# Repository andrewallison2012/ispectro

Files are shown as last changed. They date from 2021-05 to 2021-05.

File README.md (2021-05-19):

# Ispectro
Open-source software for an Impedance Spectroscopy (BIS) Device based on Arduino.

To in a venv install:
```
pip install -r requirements.txt 
```

To run:
```
python main.py
```

Qt5 Designer file:
```
ispectro_xml.ui
```

Persistent Settings:
```
config.ini
```

Generate pyQt5 Ui_MainWindow and QtBaseClass classes for python
```
pyuic5 -x ispectro_xml.ui -o ispectro_xml.py
```

Arduino Code for BIS Device
```
firmware.ino
```

KiCad Schematics for Device:
```
impedance_777/impedance_777_r1.pro
```

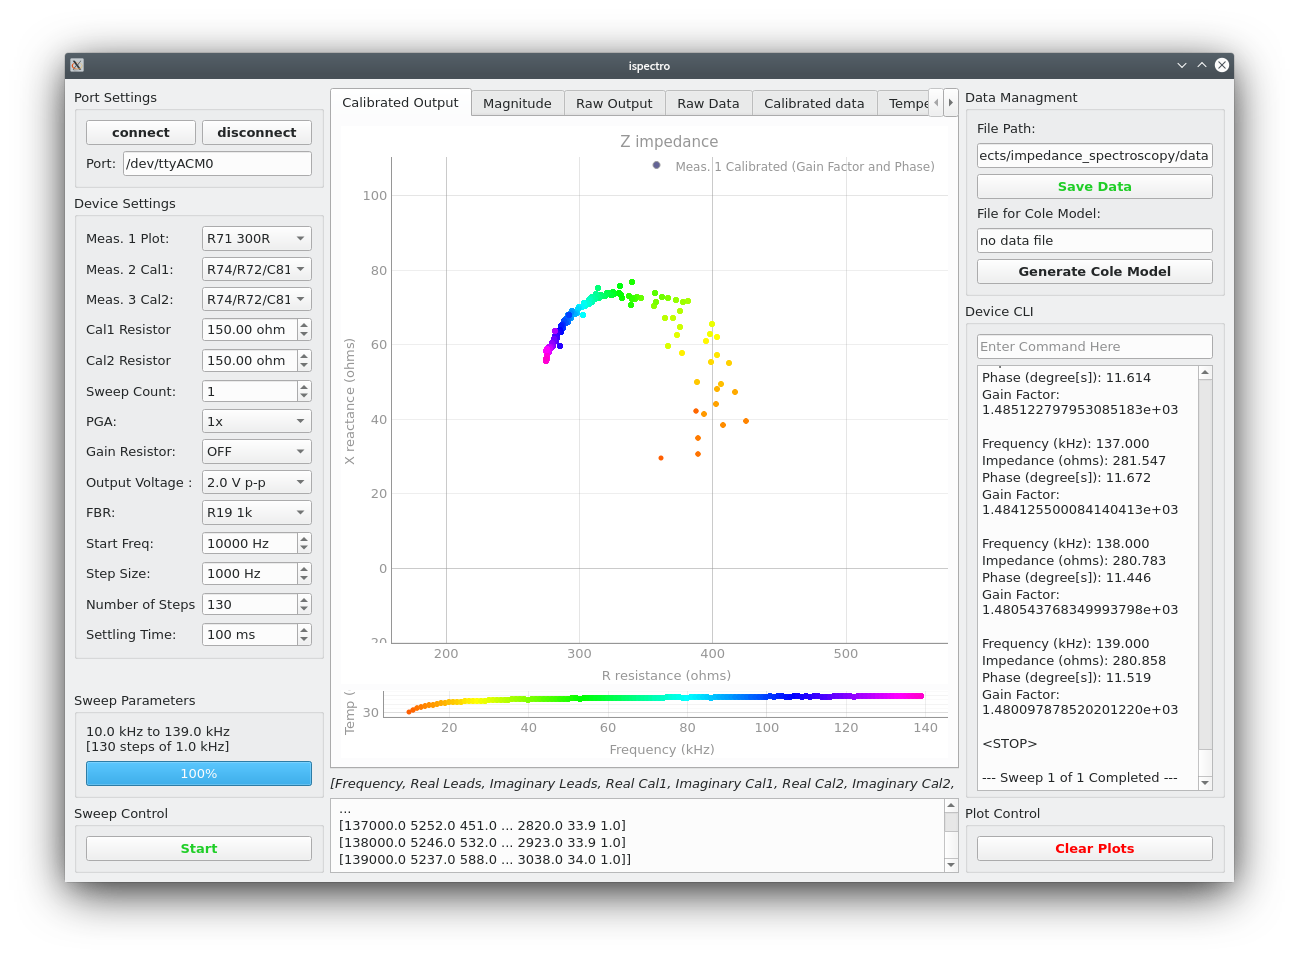
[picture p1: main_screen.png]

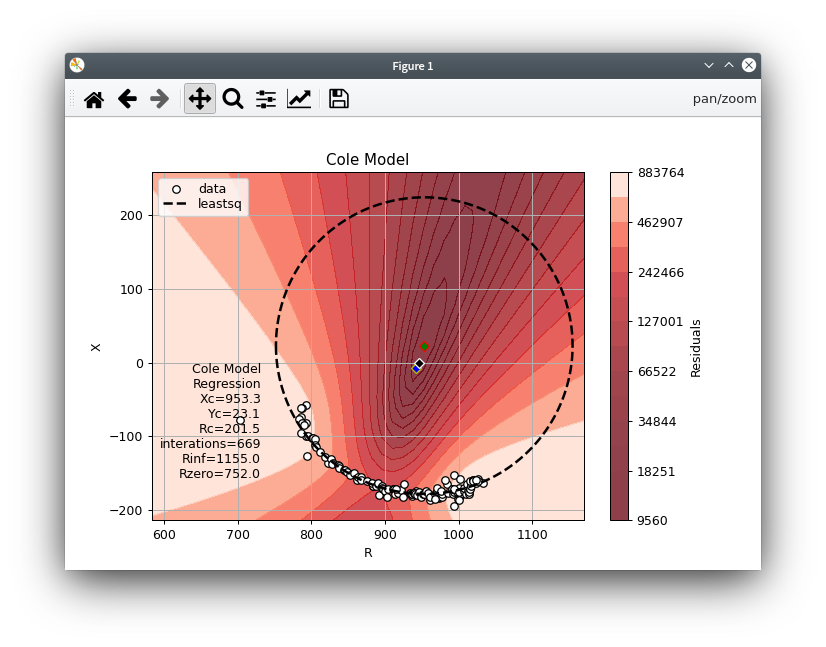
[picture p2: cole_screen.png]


> Software and firmware for an Impedance Spectroscopy (BIS) Device based on ATMEGA2560 (Arduino) and AD5933
>
> Copyright (C) 2021  Andrew Allison
>
> This program is free software: you can redistribute it and/or modify it under the terms of the GNU Affero General Public License as published by the Free Software Foundation, either version 3 of the License, or (at your option) any later version.
>
> This program is distributed in the hope that it will be useful, but WITHOUT ANY WARRANTY; without even the implied warranty of MERCHANTABILITY or FITNESS FOR A PARTICULAR PURPOSE.  See the GNU Affero General Public License for more details.
>
> You should have received a copy of the GNU Affero General Public License along with this program.  If not, see <http://www.gnu.org/licenses/>.



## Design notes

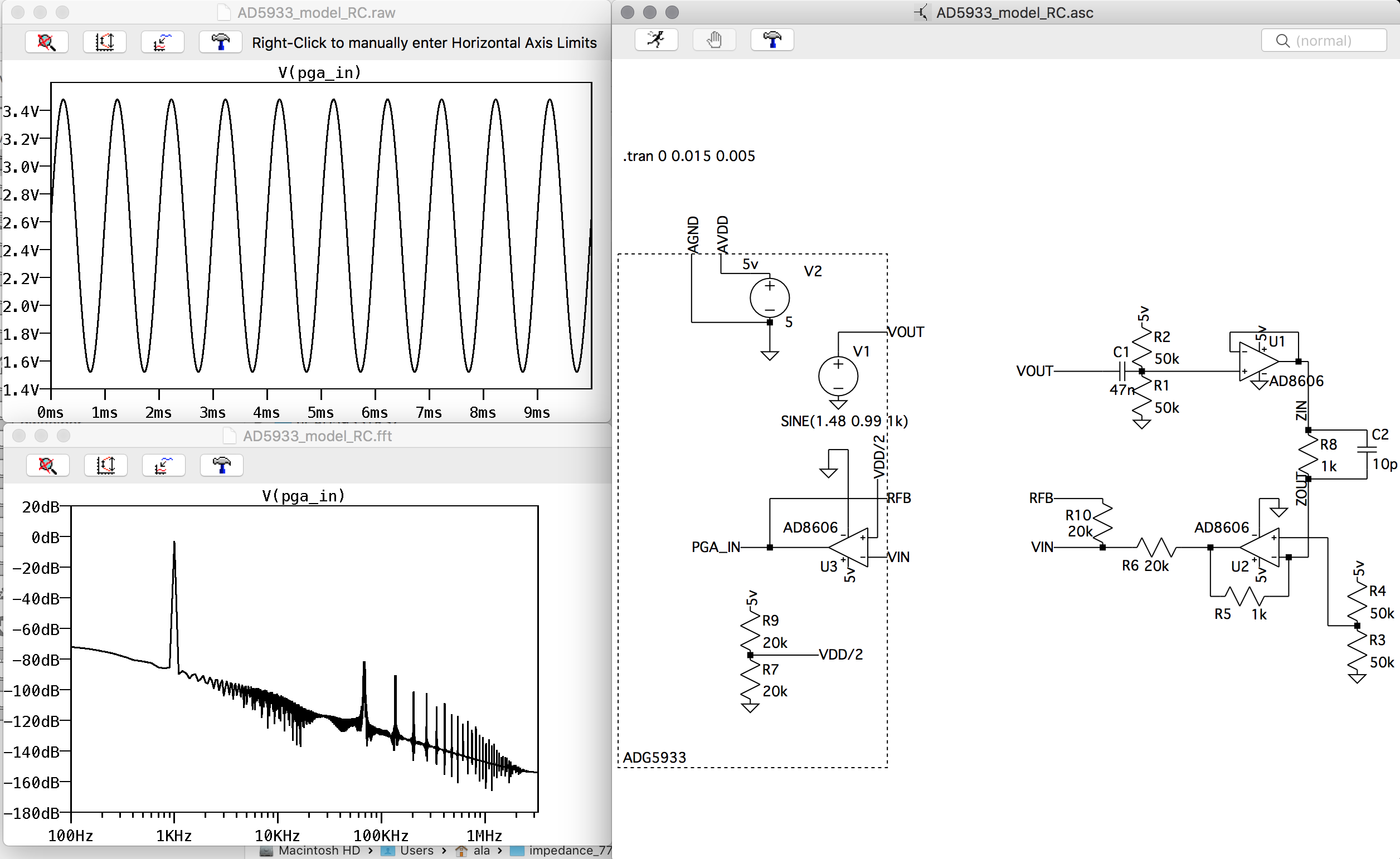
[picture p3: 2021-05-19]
impedance_777/impedance-demo/Screen Shot 2019-07-26 at 9.22.20 PM.png

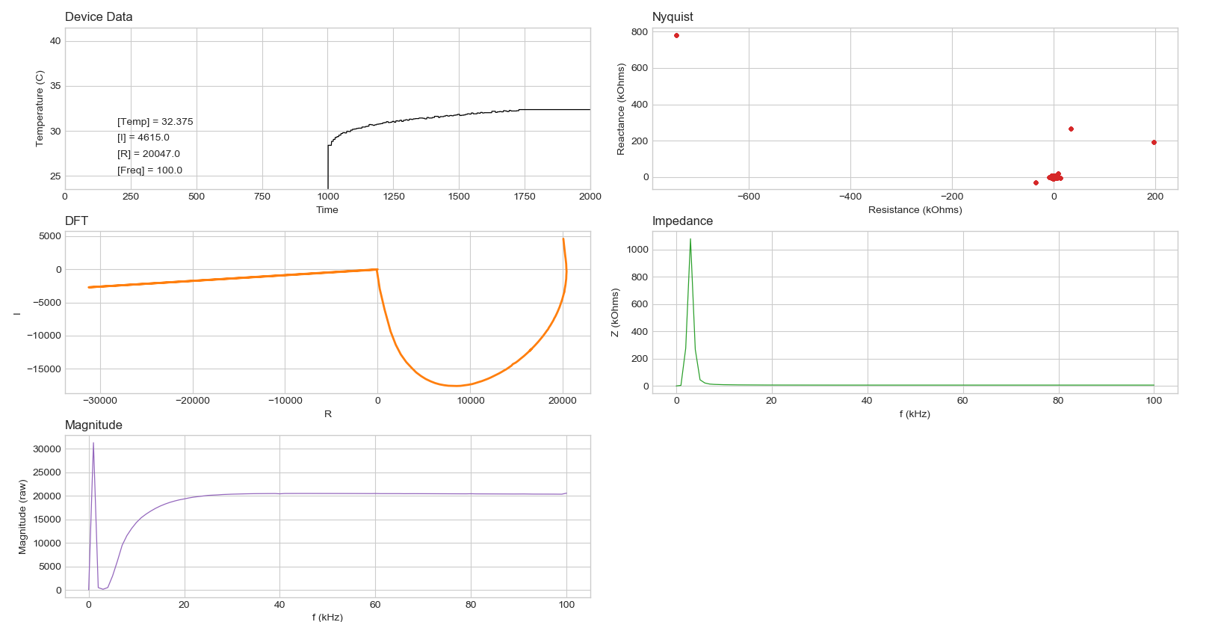
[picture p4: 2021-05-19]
impedance_777/screen-shots/cal6-image.png

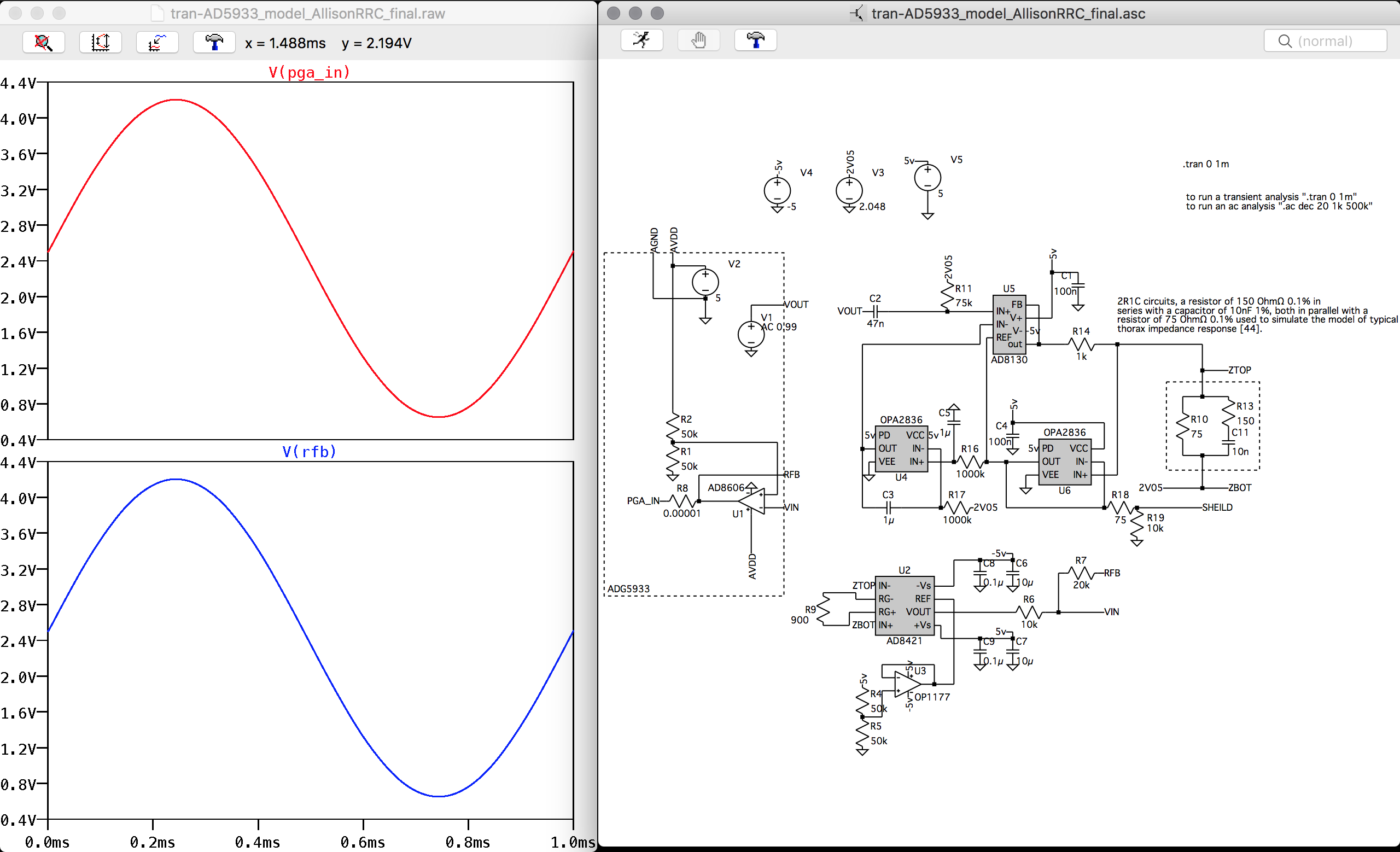
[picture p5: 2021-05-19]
impedance_777/impedance-demo/Screen Shot 2019-10-14 at 8.44.11 PM.png

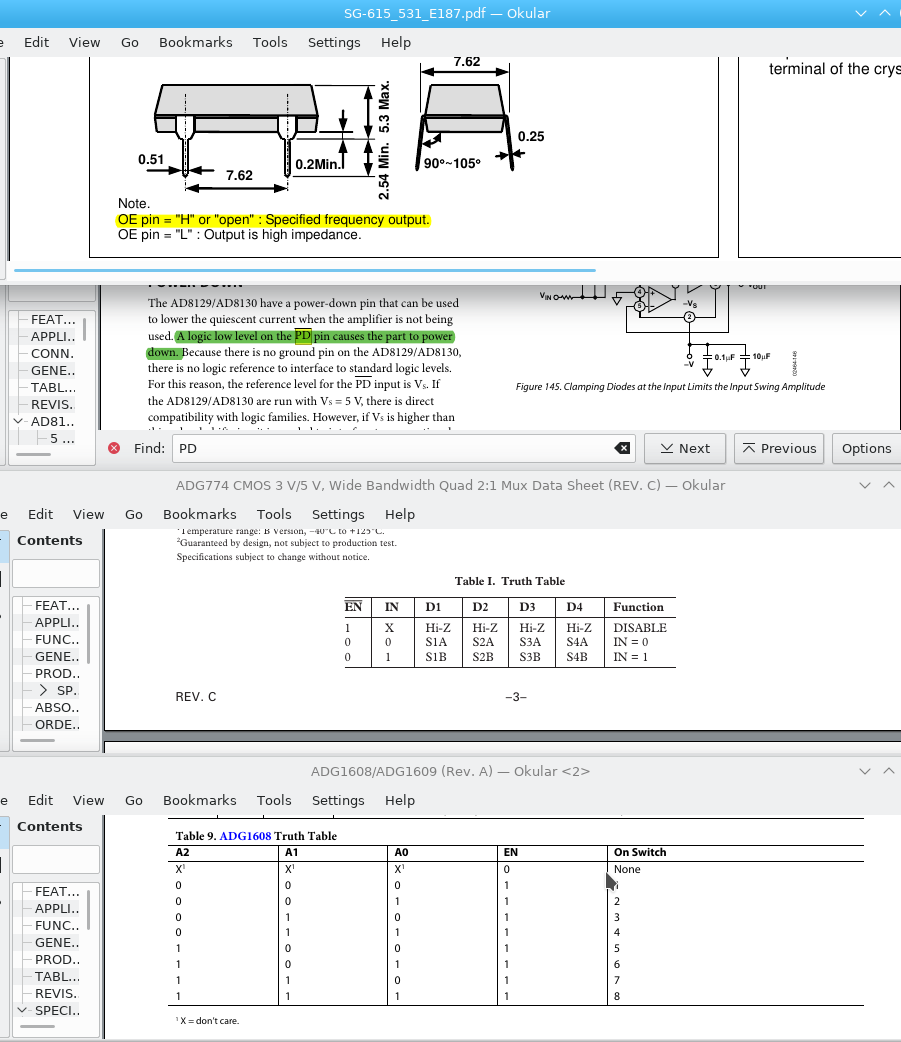
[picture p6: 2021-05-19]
impedance_777/pin_settings_for_impedance_device.png

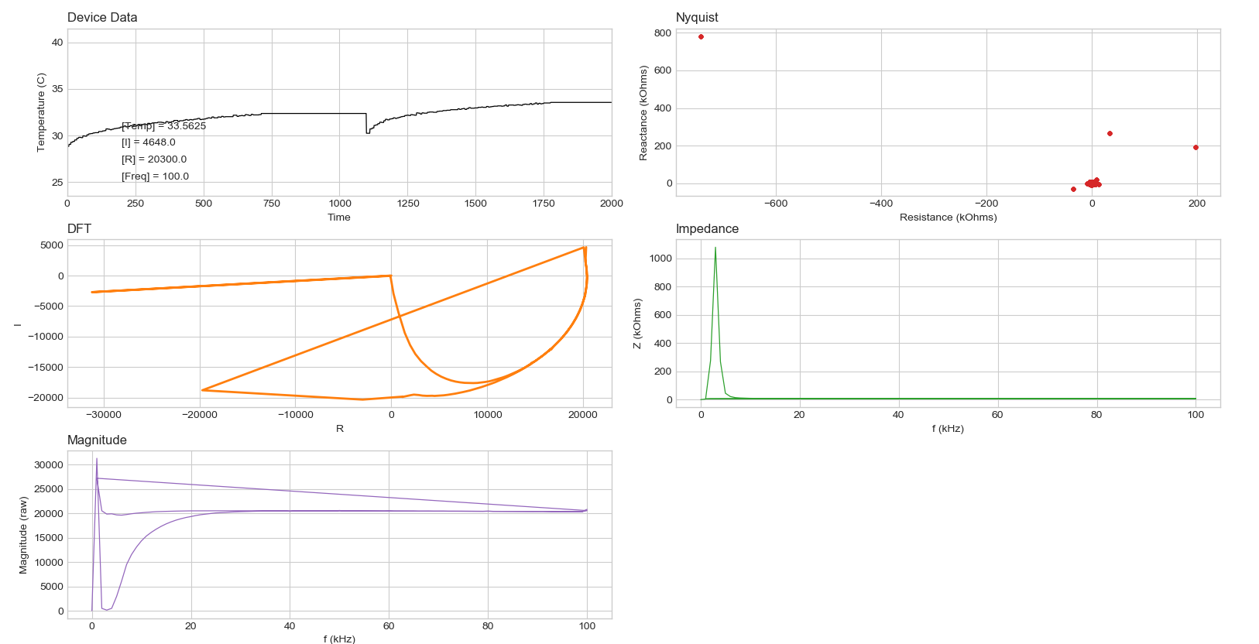
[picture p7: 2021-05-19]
impedance_777/screen-shots/cal6-cal7image.png

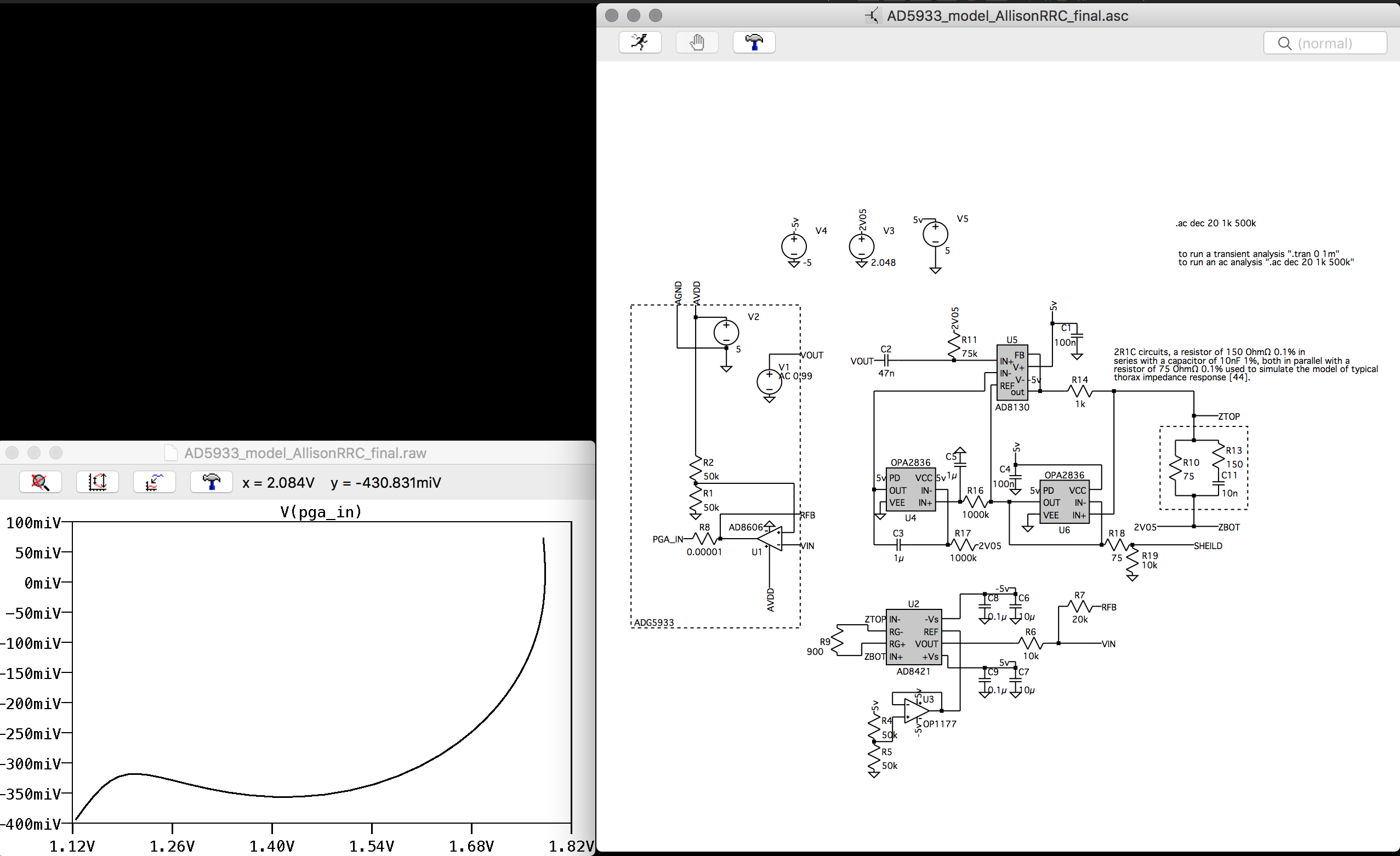
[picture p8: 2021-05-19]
impedance_777/impedance-demo/Screen Shot 2019-08-03 at 2.26.41 PM.png

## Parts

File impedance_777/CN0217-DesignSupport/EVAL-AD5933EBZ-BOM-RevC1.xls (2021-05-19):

Analog Bill Of Materials for EVAL-AD5933EBZ (Rev C1) 13/3/12
Name | Part Description | Value | Tolerance | PCB Decal | SMD | Layer Name | PART DESC | MFG #1 | Part Number | STOCK CODE
C1 | CAP | DNI |  | CAP\MR04 | No | Top | Place holder | n/a | n/a | Not Inserted
C2 | CAP | DNI |  | CAP\MR04 | No | Top | Place holder | n/a | n/a | Not Inserted
C3 | CAP | DNI |  | CAP\MR04 | No | Top | Place holder | n/a | n/a | Not Inserted
Z | CAP | DNI |  | CAP\MR04 | No | Top | Place holder - Insert 2 Wire-Wrap Pins | Analog Issue | 73017015 | ADI Stores 73017015 (x2)
C5 | CAP+ | 10uF |  | CAP\TAJ_B | Yes | Top | 10V Tantalum Capacitor | AVX | TAJB106K016R | FEC 498-737
C6 | CAP | 0.1uF | 10% | 0603 | Yes | Top | 50V X7R SMD Ceramic Capacitor | AVX | 06035C104KAT2A | FEC 1301804
C7 | CAP | 47nF | 10% | R1/8W | No | Top | CAPACITOR, 47NF, 50V, ThruHole | Multicomp | MCRR50473X7RK0050 | FEC 1216439
C8 | CAP | 0.1uF | 10% | 0603 | Yes | Top | 50V X7R SMD Ceramic Capacitor | AVX | 06035C104KAT2A | FEC 1301804
C9 | CAP | 10uF |  | 0805 | Yes | Top | X5R Ceramic Capacitor | Yageo | CC0805KKX5R6BB106 | FEC 9402136
C10 | CAP | 0.1uF | 10% | 0603 | Yes | Top | 50V X7R SMD Ceramic Capacitor | AVX | 06035C104KAT2A | FEC 1301804
C11 | CAP | 10uF |  | 0805 | Yes | Top | X5R Ceramic Capacitor | Yageo | CC0805KKX5R6BB106 | FEC 9402136
C12 | CAP | 0.1uF | 10% | 0603 | Yes | Top | 50V X7R SMD Ceramic Capacitor | AVX | 06035C104KAT2A | FEC 1301804
C13 | CAP | 0.1uF | 10% | 0603 | Yes | Top | 50V X7R SMD Ceramic Capacitor | AVX | 06035C104KAT2A | FEC 1301804
C14 | CAP | 2.2uF |  | 0603 | Yes | Top | 6.3V X5R SMD Ceramic Capacitor | Yageo | CC0603KRX5R5BB225 | FEC 9402101
C15 | CAP | 0.1uF | 10% | 0603 | Yes | Top | 50V X7R SMD Ceramic Capacitor | AVX | 06035C104KAT2A | FEC 1301804
C16 | CAP | 0.1uF | 10% | 0603 | Yes | Top | 50V X7R SMD Ceramic Capacitor | AVX | 06035C104KAT2A | FEC 1301804
C17 | CAP | 0.1uF | 10% | 0603 | Yes | Top | 50V X7R SMD Ceramic Capacitor | AVX | 06035C104KAT2A | FEC 1301804
C18 | CAP | 0.1uF | 10% | 0603 | Yes | Top | 50V X7R SMD Ceramic Capacitor | AVX | 06035C104KAT2A | FEC 1301804
C19 | CAP | 0.1uF | 10% | 0603 | Yes | Top | 50V X7R SMD Ceramic Capacitor | AVX | 06035C104KAT2A | FEC 1301804
C20 | CAP | 0.1uF | 10% | 0603 | Yes | Top | 50V X7R SMD Ceramic Capacitor | AVX | 06035C104KAT2A | FEC 1301804
C21 | CAP | 0.1uF | 10% | 0603 | Yes | Top | 50V X7R SMD Ceramic Capacitor | AVX | 06035C104KAT2A | FEC 1301804
C22 | CAP | 10uF |  | 0805 | Yes | Top | X5R Ceramic Capacitor | Yageo | CC0805KKX5R6BB106 | FEC 9402136
C23 | CAP | 0.1uF | 10% | 0603 | Yes | Top | 50V X7R SMD Ceramic Capacitor | AVX | 06035C104KAT2A | FEC 1301804
C24 | CAP | 0.1uF | 10% | 0603 | Yes | Top | 50V X7R SMD Ceramic Capacitor | AVX | 06035C104KAT2A | FEC 1301804
C25 | CAP | 10uF |  | 0805 | Yes | Top | X5R Ceramic Capacitor | Yageo | CC0805KKX5R6BB106 | FEC 9402136
C26 | CAP | 0.1uF | 10% | 0603 | Yes | Top | 50V X7R SMD Ceramic Capacitor | AVX | 06035C104KAT2A | FEC 1301804
C27 | CAP | 0.1uF | 10% | 0603 | Yes | Top | 50V X7R SMD Ceramic Capacitor | AVX | 06035C104KAT2A | FEC 1301804
C28 | CAP | 22pF | 5% | 0603 | Yes | Top | 50V NPO SMD Ceramic Capacitor | Yageo | CC0603JRNPO9BN220 | FEC 722-005
C29 | CAP | 22pF | 5% | 0603 | Yes | Top | 50V NPO SMD Ceramic Capacitor | Yageo | CC0603JRNPO9BN220 | FEC 722-005
C30 | CAP | 0.1uF | 10% | 0603 | Yes | Top | 50V X7R SMD Ceramic Capacitor | AVX | 06035C104KAT2A | FEC 1301804
C31 | CAP | 10uF |  | 0805 | Yes | Top | X5R Ceramic Capacitor | Yageo | CC0805KKX5R6BB106 | FEC 9402136
C32 | CAP | 10uF |  | 0805 | Yes | Top | X5R Ceramic Capacitor | Yageo | CC0805KKX5R6BB106 | FEC 9402136
C33 | CAP | 0.1uF | 10% | 0603 | Yes | Top | 50V X7R SMD Ceramic Capacitor | AVX | 06035C104KAT2A | FEC 1301804
C34 | CAP | 0.1uF | 10% | 0603 | Yes | Top | 50V X7R SMD Ceramic Capacitor | AVX | 06035C104KAT2A | FEC 1301804
C35 | CAP | 10uF |  | 0805 | Yes | Top | X5R Ceramic Capacitor | Yageo | CC0805KKX5R6BB106 | FEC 9402136
C36 | CAP | 0.1uF | 10% | 0603 | Yes | Top | 50V X7R SMD Ceramic Capacitor | AVX | 06035C104KAT2A | FEC 1301804
CLK1 | SMB |  |  | SMB | No | Top | SMB SOCKET | Tyco | 1-1337482-0 | FEC 1206013
D4 | LED |  |  | LED-0805 | Yes | Top | Green LED | Avago | HSMG-C170 | FEC 5790852
GL1 | GROUNDLINK |  |  | COMPONENTLINK | Yes | Bottom | Copper Short | n/a | n/a | n/a
J1 | USB-MINI-B |  |  | USB-MINI-B | Yes | Top | USB Mini-B Connector | Molex | 56579-0576 | FEC 9786490
J2 | CON\POWER |  |  | CON\POWER | No | Top | 2 Pin Terminal Block (5mm Pitch) | Camden | CTB5000/2 | FEC 151-789
LK1 | JUMPER |  |  | SIP-2P | No | Top | Jumper Block, 2 Pins 0.1" Spacing | Harwin | M20-9990246 | FEC 1022247 & 150-411
LK2 | JUMPER |  |  | SIP-2P | No | Top | Jumper Block, 2 Pins 0.1" Spacing | Harwin | M20-9990246 | FEC 1022247 & 150-411
LK3 | JUMPER |  |  | SIP-2P | No | Top | Jumper Block, 2 Pins 0.1" Spacing | Harwin | M20-9990246 | FEC 1022247 & 150-411
LK4 | JUMPER |  |  | SIP-2P | No | Top | Jumper Block, 2 Pins 0.1" Spacing | Harwin | M20-9990246 | FEC 1022247 & 150-411
LK5 | JUMPER |  |  | SIP-2P | No | Top | Jumper Block, 2 Pins 0.1" Spacing | Harwin | M20-9990246 | FEC 1022247 & 150-411
LK6 | JUMPER2\SIP3 |  |  | LINK-3P | No | Top | Jumper Block, 3 Pins 0.1" Spacing | Harwin | M20-9990246 | FEC 1022247 & 150-411
R1 | RES0603 | 49K9 | 1% | 0603 | Yes | Top | SMD Resistor | Multicomp | MC 0.063W 0603 1% 49K9 | FEC 1170955
R2 | RES0603 | 49K9 | 1% | 0603 | Yes | Top | SMD Resistor | Multicomp | MC 0.063W 0603 1% 49K9 | FEC 1170955
RFB | RES | DNI | n/a | R1/8W | No | Top | Place holder - Insert 2 Wire-Wrap Pins | Analog Issue | 73017015 | ADI Stores 73017015 (x2)
R4 | RES0603 | 20K | 0.10% | 0603 | Yes | Top | SMD Resistor (0.1%) | Panasonic | ERA3AEB203V | FEC 9330771
R5 | RES0603 | 20K | 0.10% | 0603 | Yes | Top | SMD Resistor (0.1%) | Multicomp | MC 0.063W 0603 1% 20K | FEC 9330771
R6 | RES | DNI | n/a | R1/8W | No | Top | THROUGH HOLE Resistor 1/8 W | n/a | n/a | Not Inserted
R7 | RES0603 | 49K9 | 1% | 0603 | Yes | Top | SMD Resistor | Multicomp | MC 0.063W 0603 1% 49K9 | FEC 1170955
R8 | RES0603 | 49K9 | 1% | 0603 | Yes | Top | SMD Resistor | Multicomp | MC 0.063W 0603 1% 49K9 | FEC 1170955
R9 | RES | 50R | 1% | 0603 | Yes | Top | SMD Resistor | Multicomp | MC 0.063W 0603 1% 49R9 | FEC 1170658
R10 | RES | 1k |  | 0805 | Yes | Top | SMD Resistor | Multicomp | MC 0.1W 0805 1% 1K | FEC 9332383
R11 | RES | 100k | 1% | 0603 | Yes | Top | SMD Resistor | Multicomp | MC 0.063W 0603 1% 100K | FEC 9330402
R12 | RES | 100k | 1% | 0603 | Yes | Top | SMD Resistor | Multicomp | MC 0.063W 0603 1% 100K | FEC 9330402
R13 | RES | 0R | 1% | 0603 | Yes | Top | SMD Resistor | Multicomp | MC 0.063W 0603 0R | FEC 9331662
R14 | RES | 10k | 1% | 0603 | Yes | Top | SMD Resistor | Multicomp | MC 0.063W 0603 1% 10K | FEC 9330399
R15 | RES | 2k2 | 1% | 0603 | Yes | Top | SMD Resistor | Multicomp | MC 0.063W 0603 1% 2K2 | FEC 9330810
R16 | RES | 2k2 | 1% | 0603 | Yes | Top | SMD Resistor | Multicomp | MC 0.063W 0603 1% 2K2 | FEC 9330810
T1 | TESTPOINT |  |  | TESTPOINT | No | Top | TESTPOINT | Black Testpoint | 20-2137 | FEC 8731128
T2 | TESTPOINT |  |  | TESTPOINT | No | Top | TESTPOINT | Black Testpoint | 20-2137 | FEC 8731128
T3 | TESTPOINT |  |  | TESTPOINT | No | Top | TESTPOINT | Black Testpoint | 20-2137 | FEC 8731128
T5 | TESTPOINT |  |  | TESTPOINT | No | Top | TESTPOINT | Black Testpoint | 20-2137 | FEC 8731128
T6 | TESTPOINT |  |  | TESTPOINT | No | Top | TESTPOINT | Black Testpoint | 20-2137 | FEC 8731128
T7 | TESTPOINT |  |  | TESTPOINT | No | Top | TESTPOINT | Black Testpoint | 20-2137 | FEC 8731128
T8 | TESTPOINT |  |  | TESTPOINT | No | Top | TESTPOINT | Black Testpoint | 20-2137 | FEC 8731128
U1 | AD8606 |  |  | SO8NB | Yes | Top | Dual Op-Amp | Analog Devices | AD8606ARZ | AD8606ARZ
U2 | AD5933 |  |  | SSOP16 | Yes | Top |  | Analog Devices | AD5933YRSZ | AD5933YRSZ
U3 | CY7C68013-CSP |  |  | LFCSP-56 | Yes | Top | USB Microcontroller | Cypress Semiconductor | CY7C68013-56LFC | Digikey 428-1669-ND
U4 | 24LC64 |  |  | SO8NB | Yes | Top | IC SERIAL EEPROM 64K 2.5V 8-SOIC | Microchip | 24LC64-I/SN | FEC 9758070
U5 | ADP3303-3.3 |  |  | SO8NB | Yes | Top | Precision Low Dropout Voltage Regulator | Analog Devices | ADP3303ARZ-3.3 | ADP3303ARZ-3.3
U6 | ADP3303-3.3 |  |  | SO8NB | Yes | Top | Precision Low Dropout Voltage Regulator | Analog Devices | ADP3303ARZ-3.3 | ADP3303ARZ-3.3
Y1 | XTAL-CM309S | 24 MHz |  | XTAL_CM309S | Yes | Top | CM309S SMD Crystal | AEL | X24M000000S244 | FEC 9509658
Y2 | AEL-4303 | 16Mhz |  | AEL-4303 | Yes | Top | 3.3V 16MHz Clock Oscillator | AEL |  | AEL 4313AI | Contact: Laura Stockwood / Robert Newbold at Ael | laura.stockwood@aelcrystals.co.uk
 |  |  |  |  |  |  |  |  |  |  |  | robert.newbold@aelcrystals.co.uk
 |  |  |  |  |  |  | Stick on Feet x4 |  |  | FEC 651-813
 | Not Inserted Parts |  |  |  |  |  | Anti-Static bag - Board to be packed in bag |  |  | FEC 522-764
 | ADI Supplied Parts |  |  |  |  |  | USB A to Mini-B Cable |  |  | Digikey 167-1011-ND
 |  |  |  |  |  |  | Eval Kit Box |  |  | Europacks K-645/1
 |  |  |  |  |  |  | Packing Material |  |  | Bubble Wrap
 |  |  |  |  |  |  | Software Warning Sticker
 |  |  |  |  |  |  | Distribution CD
 |  |  |  |  |  |  | Barcode Label | EVAL-AD5933EBZ

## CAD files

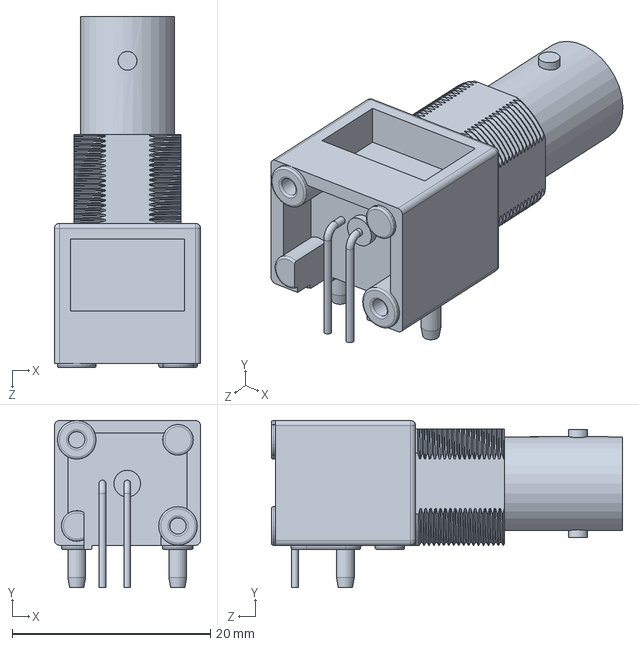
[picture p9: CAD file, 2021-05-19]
impedance_777/BNC Connector/BNC Connector.SLDPRT
14.8 x 16.9 x 35.5 mm

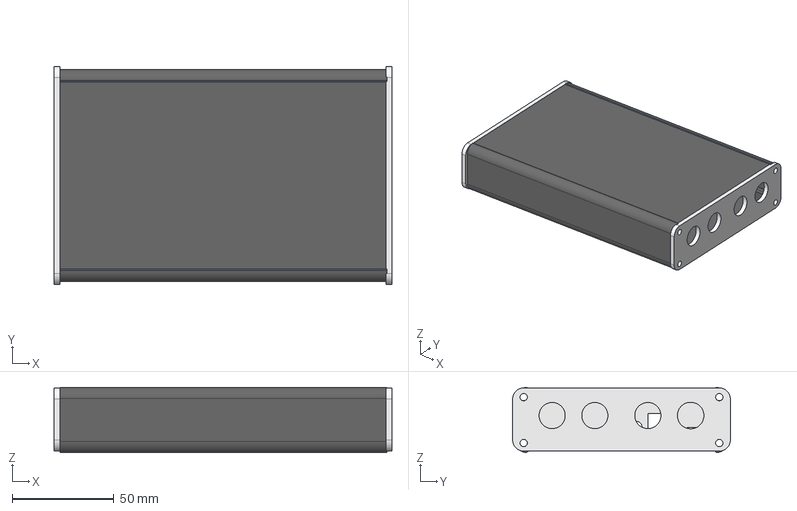
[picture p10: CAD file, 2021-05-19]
impedance_777/freeCAD/end-panel-ispectro-ala.FCStd
165.9 x 106.9 x 32.0 mm

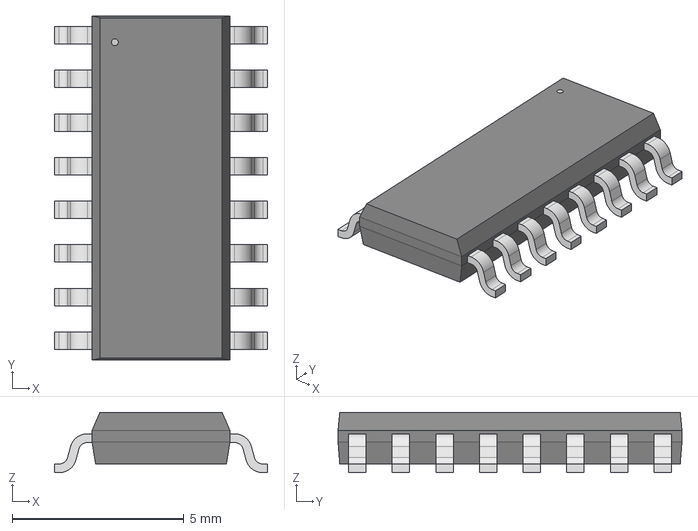
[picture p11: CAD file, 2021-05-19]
impedance_777/ul_ADG774BRZ/2019-05-09_08-00-37/STEP/R_16-L.step
6.20 x 10.0 x 1.75 mm

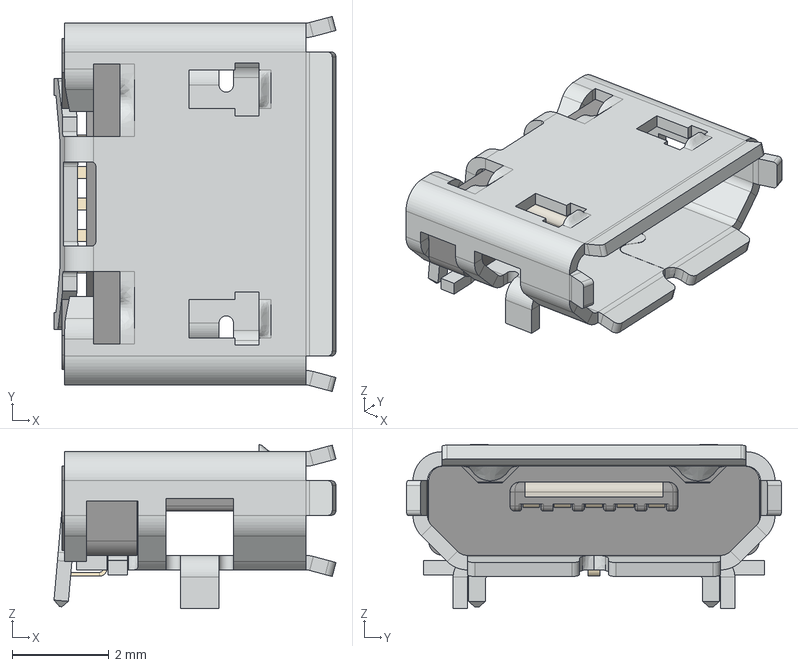
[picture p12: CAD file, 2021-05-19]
impedance_777/usb-micro-b-molex-1013594-1.snapshot.7/micro_usb_connector.stp
5.84 x 7.77 x 3.40 mm
shield
socket_housing
socket_plate
terminal x 5

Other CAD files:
impedance_777/ul_ADG774BRZ/2019-05-09_08-00-37/STEP/R_16-M.step
impedance_777/ul_ADG774BRZ/2019-05-09_08-00-37/STEP/R_16.step
impedance_777/ul_ADG774BRZ/2019-05-09_08-00-37/STL/R_16-L.stl
impedance_777/ul_ADG774BRZ/2019-05-09_08-00-37/STL/R_16-L.stp
impedance_777/ul_ADG774BRZ/2019-05-09_08-00-37/STL/R_16-M.stl
impedance_777/ul_ADG774BRZ/2019-05-09_08-00-37/STL/R_16-M.stp
impedance_777/ul_ADG774BRZ/2019-05-09_08-00-37/STL/R_16.stl
impedance_777/ul_ADG774BRZ/2019-05-09_08-00-37/STL/R_16.stp
impedance_777/usb-micro-b-molex-1013594-1.snapshot.7/micro_usb_connector.igs
impedance_777/usb-micro-b-molex-1013594-1.snapshot.7/micro_usb_connector.skp
impedance_777/usb-micro-b-molex-1013594-1.snapshot.7/micro_usb_connector.stl

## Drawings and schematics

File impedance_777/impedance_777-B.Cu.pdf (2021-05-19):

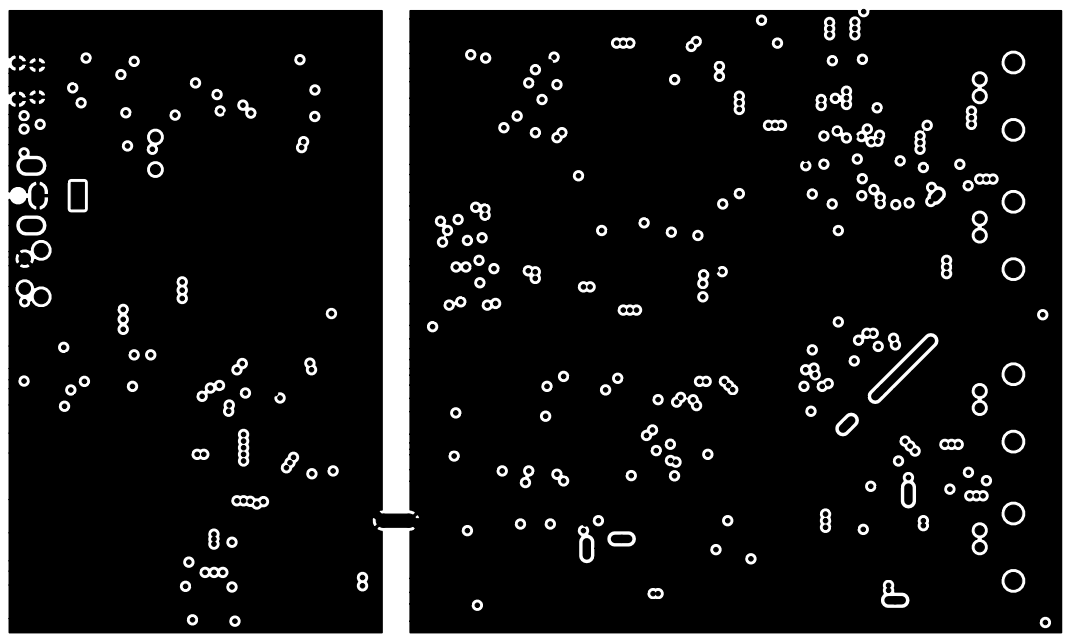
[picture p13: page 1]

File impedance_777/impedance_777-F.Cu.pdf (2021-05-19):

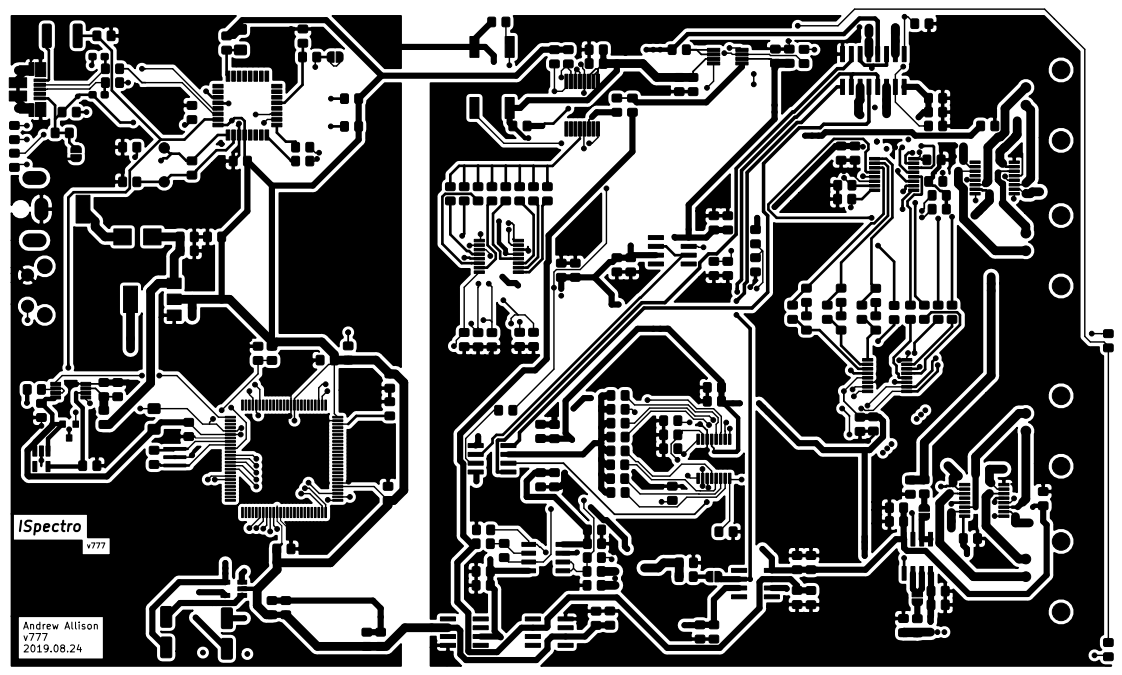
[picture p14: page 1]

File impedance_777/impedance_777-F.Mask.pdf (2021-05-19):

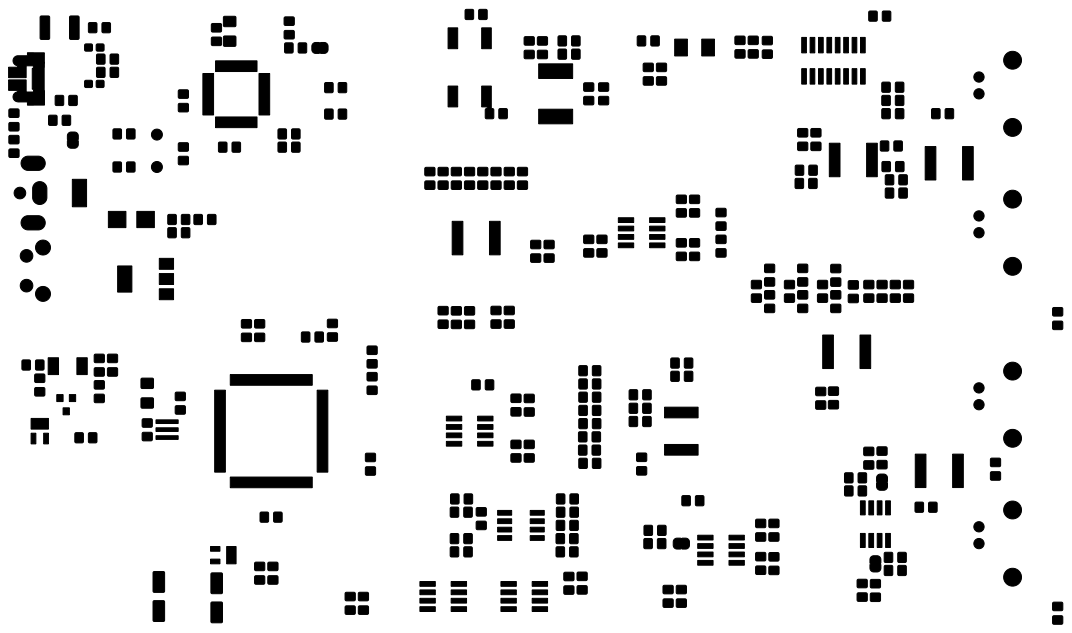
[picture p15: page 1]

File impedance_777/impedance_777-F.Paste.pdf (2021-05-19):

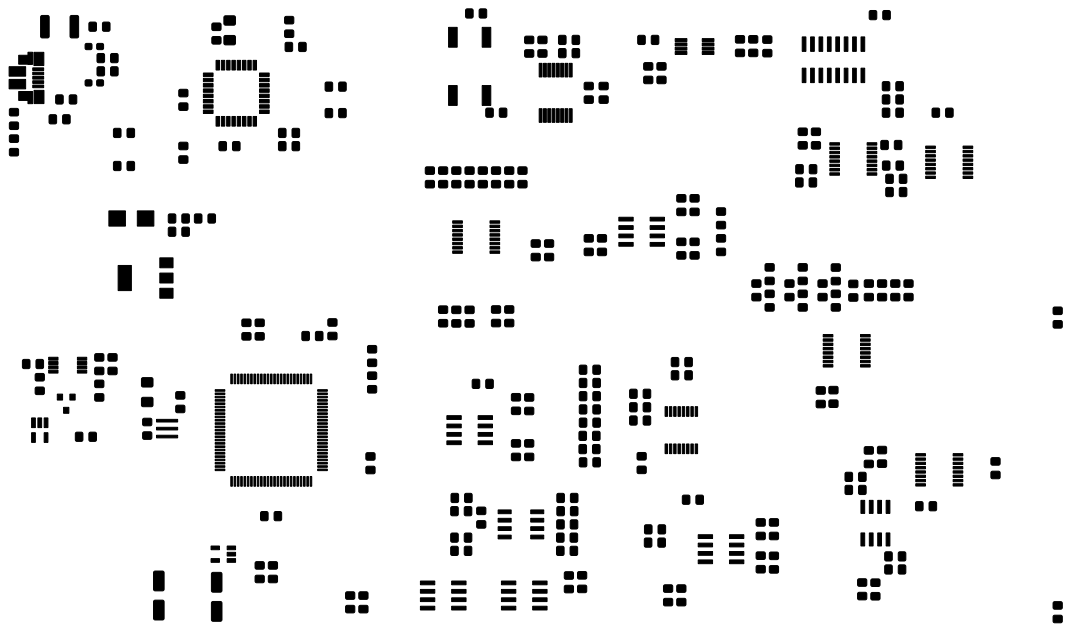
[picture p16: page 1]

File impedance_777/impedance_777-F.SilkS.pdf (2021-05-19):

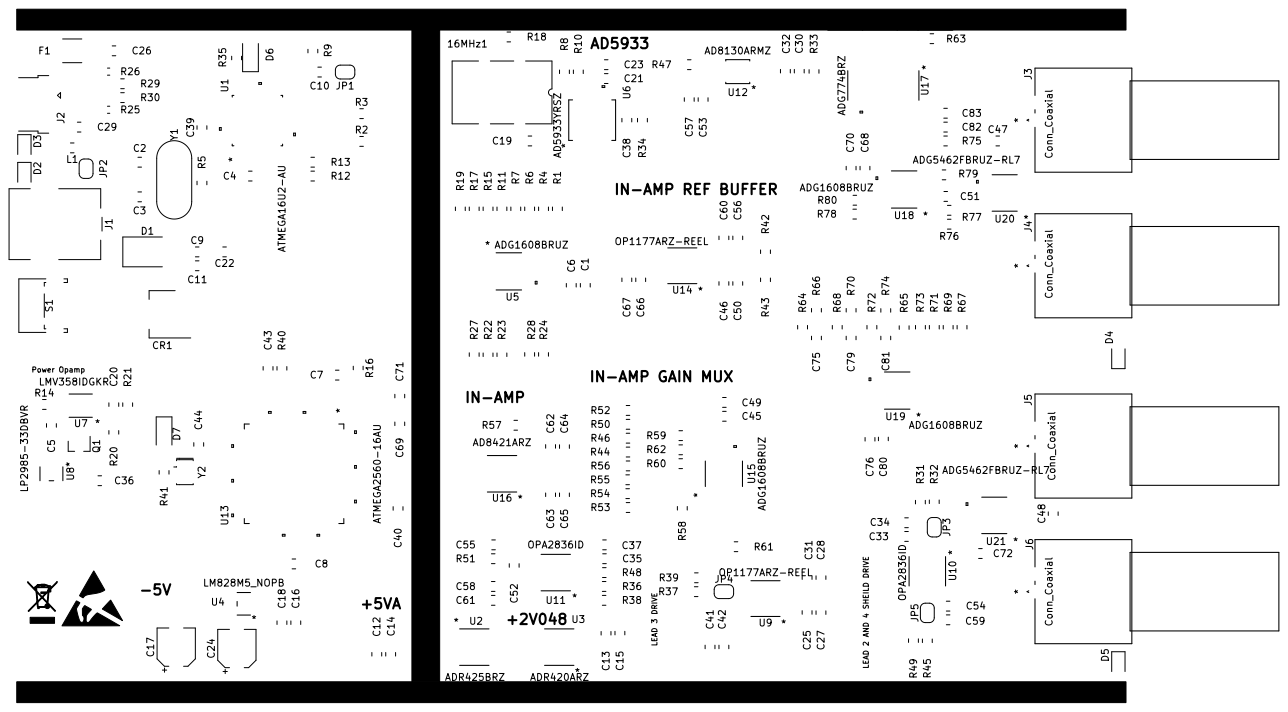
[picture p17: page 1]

IN-AMP GAIN MUX

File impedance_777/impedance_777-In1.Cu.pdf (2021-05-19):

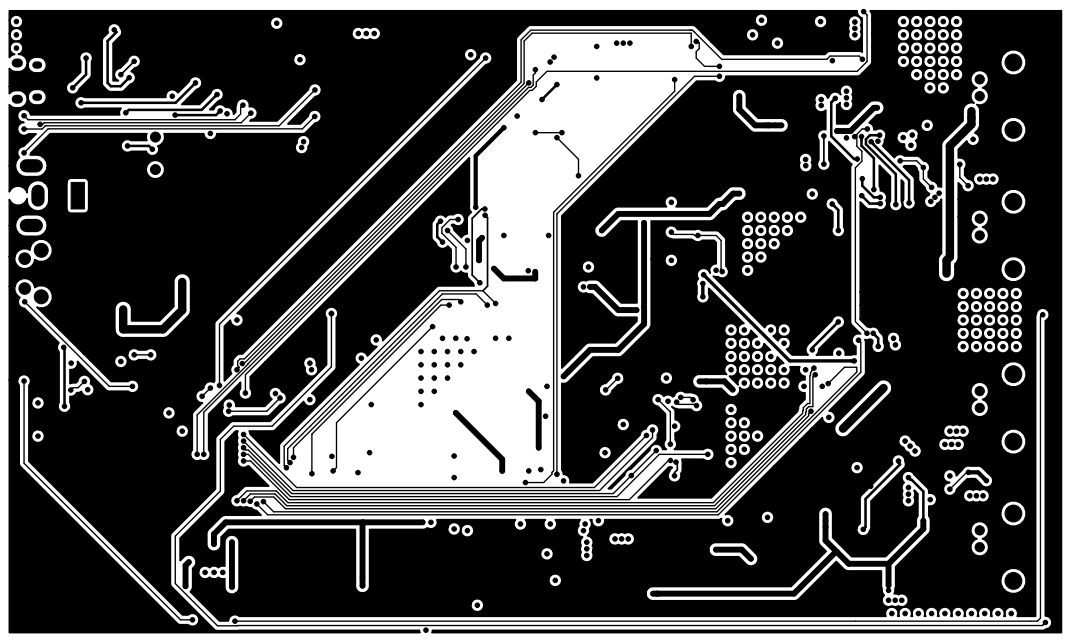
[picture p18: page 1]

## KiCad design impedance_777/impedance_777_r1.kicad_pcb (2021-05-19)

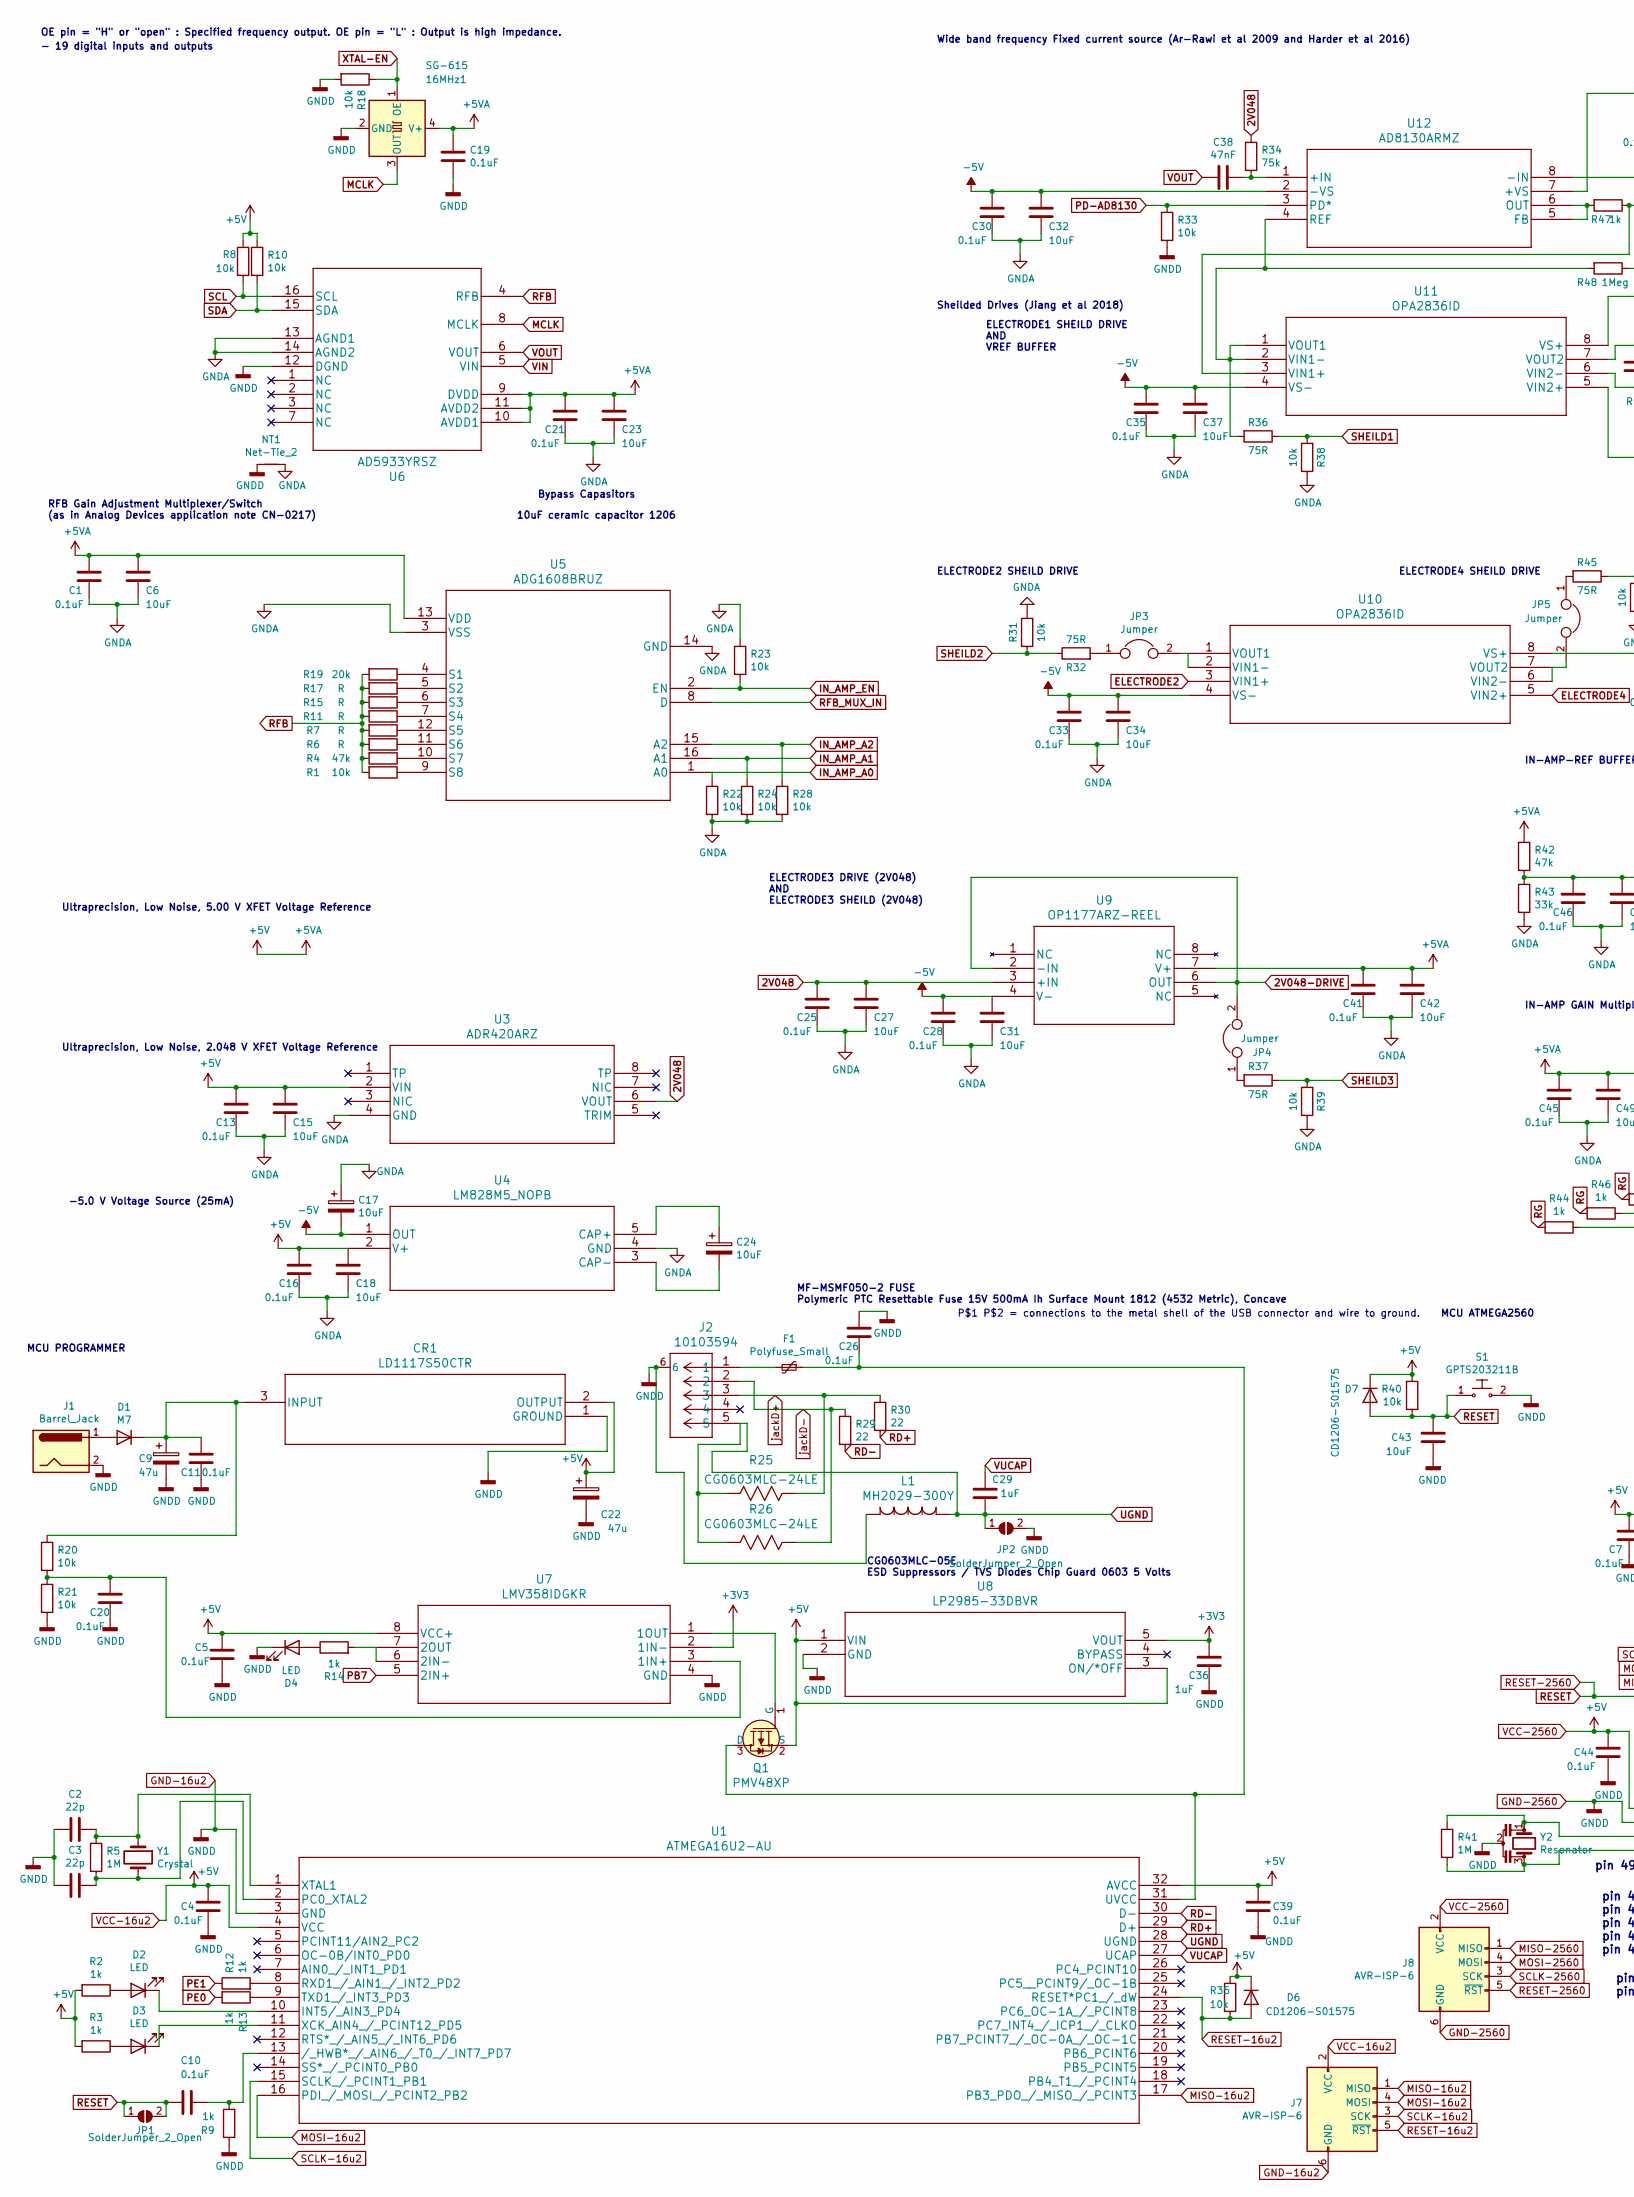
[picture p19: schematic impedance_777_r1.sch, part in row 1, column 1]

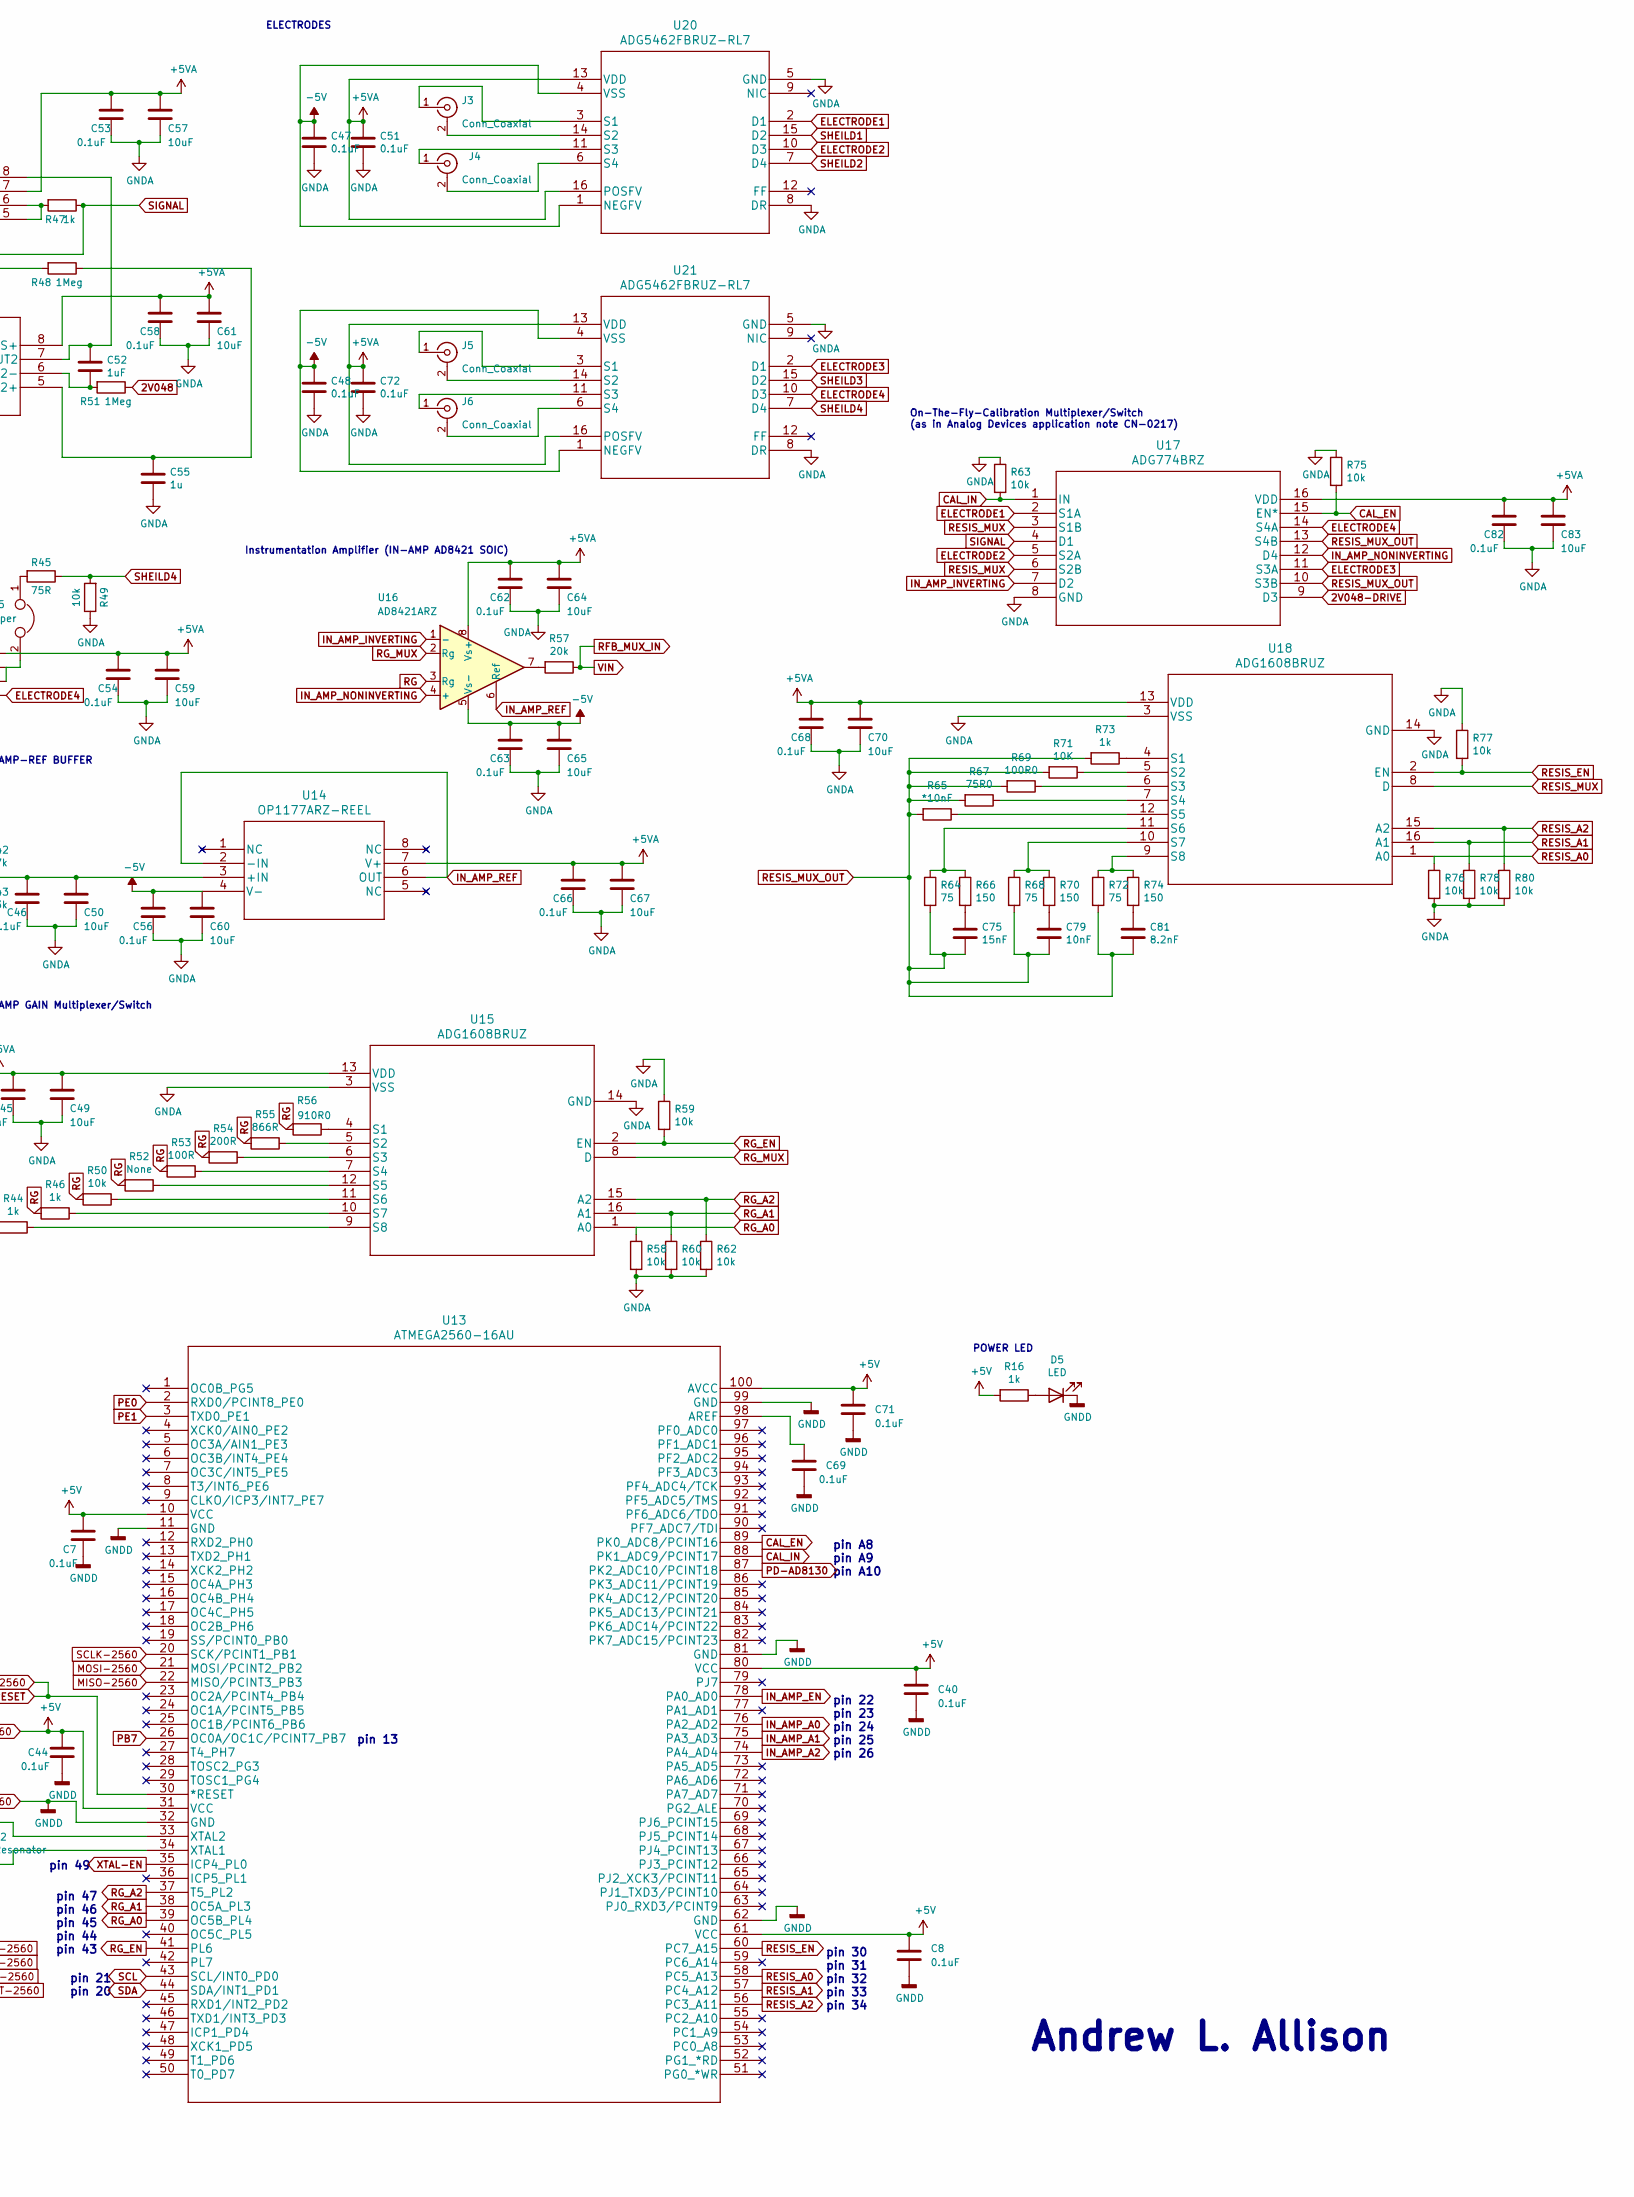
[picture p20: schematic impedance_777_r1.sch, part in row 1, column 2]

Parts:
16MHz1: SG-615; Oscillator_SMD_SeikoEpson_SG8002JA-4Pin_14.0x8.7mm
C1, C4, C5, C7, C8, C10, C11, C13, C16, C19, C20, C21, C25, C26, C28, C30, C33, C35, C39, C40, C41, C44, C45, C46, C47, C48, C51, C53, C54, C56, C58, C62, C63, C66, C68, C69, C71, C72, C82: 0.1uF; C_0805_2012Metric_Pad1.15x1.40mm_HandSolder
C2, C3: 22p; C_0805_2012Metric_Pad1.15x1.40mm_HandSolder
C6, C15, C18, C23, C27, C31, C32, C34, C37, C42, C43, C49, C50, C57, C59, C60, C61, C64, C65, C67, C70, C83: 10uF; C_0805_2012Metric_Pad1.15x1.40mm_HandSolder
C9, C22: 47u; C_0805_2012Metric_Pad1.15x1.40mm_HandSolder
C17, C24: 10uF; CP_Elec_5x5.4
C29, C36, C52: 1uF; C_0805_2012Metric_Pad1.15x1.40mm_HandSolder
C38: 47nF; C_0805_2012Metric_Pad1.15x1.40mm_HandSolder
C55: 1u; C_0805_2012Metric_Pad1.15x1.40mm_HandSolder
C75: 15nF; C_0805_2012Metric_Pad1.15x1.40mm_HandSolder
C79: 10nF; C_0805_2012Metric_Pad1.15x1.40mm_HandSolder
C81: 8.2nF; C_0805_2012Metric_Pad1.15x1.40mm_HandSolder
CR1: LD1117S50CTR; SOT-223-3_TabPin2
D1: M7; D_SMB
D2, D3, D4, D5: LED; LED_0805_2012Metric_Pad1.15x1.40mm_HandSolder
D6, D7: CD1206-S01575; D_1206_3216Metric_Pad1.42x1.75mm_HandSolder
F1: Polyfuse_Small; Fuse_1812_4532Metric_Pad1.30x3.40mm_HandSolder
J1: Barrel_Jack; BarrelJack_CUI_PJ-063AH_Horizontal
J2: 10103594; USB_Micro-B_Amphenol_10103594-0001LF_Horizontal
J3, J4, J5, J6: Conn_Coaxial; 5227161-6.pretty
J7, J8: AVR-ISP-6; IDC-Header_2x03_P2.54mm_Vertical
JP1, JP2: SolderJumper_2_Open; SolderJumper-2_P1.3mm_Open_RoundedPad1.0x1.5mm
JP3, JP4, JP5: Jumper; SolderJumper-2_P1.3mm_Open_RoundedPad1.0x1.5mm
L1: MH2029-300Y; L_0805_2012Metric_Pad1.15x1.40mm_HandSolder
NT1: Net-Tie_2; NetTie-2_SMD_Pad2.0mm
Q1: PMV48XP; SOT-23; MPN AO3401A; Digi-Key_PN 785-1001-1-ND
R1, R8, R10, R18, R20, R21, R22, R23, R24, R28, R31, R33, R35, R38, R39, R40, R49, R50, R58, R59, R60, R62, R63, R75, R76, R77, R78, R80: 10k; R_0805_2012Metric_Pad1.15x1.40mm_HandSolder
R2, R3, R9, R12, R13, R14, R16, R44, R46, R47, R73: 1k; R_0805_2012Metric_Pad1.15x1.40mm_HandSolder
R4, R42: 47k; R_0805_2012Metric_Pad1.15x1.40mm_HandSolder
R5, R41: 1M; R_0805_2012Metric_Pad1.15x1.40mm_HandSolder
R6, R7, R11, R15, R17: R; R_0805_2012Metric_Pad1.15x1.40mm_HandSolder
R19, R57: 20k; R_0805_2012Metric_Pad1.15x1.40mm_HandSolder
R25, R26: CG0603MLC-24LE; R_0603_1608Metric_Pad1.05x0.95mm_HandSolder
R29, R30: 22; R_0805_2012Metric_Pad1.15x1.40mm_HandSolder
R32, R36, R37, R45: 75R; R_0805_2012Metric_Pad1.15x1.40mm_HandSolder
R34: 75k; R_0805_2012Metric_Pad1.15x1.40mm_HandSolder
R43: 33k; R_0805_2012Metric_Pad1.15x1.40mm_HandSolder
R48, R51: 1Meg; R_0805_2012Metric_Pad1.15x1.40mm_HandSolder
R52: None; R_0805_2012Metric_Pad1.15x1.40mm_HandSolder
R53: 100R; R_0805_2012Metric_Pad1.15x1.40mm_HandSolder
R54: 200R; R_0805_2012Metric_Pad1.15x1.40mm_HandSolder
R55: 866R; R_0805_2012Metric_Pad1.15x1.40mm_HandSolder
R56: 910R0; R_0805_2012Metric_Pad1.15x1.40mm_HandSolder
R64, R68, R72: 75; R_0805_2012Metric_Pad1.15x1.40mm_HandSolder
R65: *10nF; R_0805_2012Metric_Pad1.15x1.40mm_HandSolder
R66, R70, R74: 150; R_0805_2012Metric_Pad1.15x1.40mm_HandSolder
R67: 75R0; R_0805_2012Metric_Pad1.15x1.40mm_HandSolder
R69: 100R0; R_0805_2012Metric_Pad1.15x1.40mm_HandSolder
R71: 10K; R_0805_2012Metric_Pad1.15x1.40mm_HandSolder
S1: GPTS203211B; SW_Tactile_SPST_Angled_PTS645Vx58-2LFS; MPN GPTS203211B; Digi-Key_PN CW181-ND
U1: ATMEGA16U2-AU
U3: ADR420ARZ
U4: LM828M5_NOPB; LM828M5&slash_NOPB
U5, U15, U18: ADG1608BRUZ
U6: AD5933YRSZ
U7: LMV358IDGKR
U8: LP2985-33DBVR
U9, U14: OP1177ARZ-REEL
U10, U11: OPA2836ID
U12: AD8130ARMZ
U13: ATMEGA2560-16AU
U16: AD8421ARZ
U17: ADG774BRZ
U20, U21: ADG5462FBRUZ-RL7
Y1: Crystal; Crystal_HC18-U_Vertical
Y2: Resonator; Resonator_SMD_muRata_CSTxExxV-3Pin_3.0x1.1mm_HandSoldering

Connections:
2V048: C25.1, C27.1, R34.1, R51.1, U3.6 (VOUT), U9.3 (+IN)
2V048-DRIVE: JP4.2, U9.2 (-IN), U9.6 (OUT), U17.9 (D3)
+3V3: C36.1, U7.2 (1IN-), U8.5 (VOUT)
-5V: C17.2, C28.1, C30.1, C31.1, C32.1, C33.1, C34.1, C35.1, C37.1, C47.1, C48.1, C56.1, C60.1, C63.1, C65.1, U4.1 (OUT), U9.4 (V-), U10.4 (VS-), U11.4 (VS-), U12.2 (-VS), U14.4 (V-), U16.5 (Vs-), U20.1 (NEGFV), U20.4 (VSS), U21.1 (NEGFV), U21.4 (VSS)
CAL_EN: R75.2, U13.89 (PK0_ADC8/PCINT16), U17.15 (EN*)
CAL_IN: R63.2, U13.88 (PK1_ADC9/PCINT17), U17.1 (IN)
ELECTRODE1: U17.2 (S1A), U20.2 (D1)
ELECTRODE2: U10.3 (VIN1+), U17.5 (S2A), U20.10 (D3)
ELECTRODE3: U17.11 (S3A), U21.2 (D1)
ELECTRODE4: U10.5 (VIN2+), U17.14 (S4A), U21.10 (D3)
GND-16u2: 16MHz1.2 (GND), C2.2, C3.2, C4.2, C5.2, C7.2, C8.2, C9.2, C11.2, C19.2, C20.2, C22.2, C26.1, C36.2, C39.2, C40.2, C43.2, C44.2, C69.2, C71.2, CR1.1 (GROUND), D4.1 (K), D5.1 (K), J1.2, J2.6, J7.6 (GND), J8.6 (GND), JP2.2 (B), L1.2, NT1.1, R9.1, R18.2, R21.2, R33.2, S1.2, U1.3 (GND), U6.12 (DGND), U7.4 (GND), U8.2 (GND), U13.11 (GND), U13.32 (GND), U13.62 (GND), U13.81 (GND), U13.99 (GND), Y2.2
GNDA: C1.2, C6.2, C13.2, C15.2, C16.2, C17.1, C18.2, C21.2, C23.2, C25.2, C27.2, C28.2, C30.2, C31.2, C32.2, C33.2, C34.2, C35.2, C37.2, C41.2, C42.2, C45.2, C46.2, C47.2, C48.2, C49.2, C50.2, C51.2, C53.2, C54.2, C55.1, C56.2, C57.2, C58.2, C59.2, C60.2, C61.2, C62.2, C63.2, C64.2, C65.2, C66.2, C67.2, C68.2, C70.2, C72.2, C82.2, C83.2, NT1.2, R22.2, R23.1, R24.2, R28.2, R31.1, R38.1, R39.1, R43.2, R49.1, R58.2, R59.1, R60.2, R62.2, R63.1, R75.1, R76.2, R77.1, R78.2, R80.2, U3.4 (GND), U4.4 (GND), U5.3 (VSS), U5.14 (GND), U6.13 (AGND1), U6.14 (AGND2), U15.3 (VSS), U15.14 (GND), U17.8 (GND), U18.3 (VSS), U18.14 (GND), U20.5 (GND), U20.8 (DR), U21.5 (GND), U21.8 (DR)
IN_AMP_A0: R22.1, U5.1 (A0), U13.76 (PA2_AD2)
IN_AMP_A1: R24.1, U5.16 (A1), U13.75 (PA3_AD3)
IN_AMP_A2: R28.1, U5.15 (A2), U13.74 (PA4_AD4)
IN_AMP_EN: R23.2, U5.2 (EN), U13.78 (PA0_AD0)
IN_AMP_INVERTING: U16.1 (-), U17.7 (D2)
IN_AMP_NONINVERTING: U16.4 (+), U17.12 (D4)
IN_AMP_REF: U14.2 (-IN), U14.6 (OUT), U16.6 (Ref)
MCLK: 16MHz1.3 (OUT), U6.8 (MCLK)
MISO-16u2: J7.1 (MISO), U1.17 (PB3_PDO_/_MISO_/_PCINT3)
MISO-2560: J8.1 (MISO), U13.22 (MISO/PCINT3_PB3)
MOSI-16u2: J7.4 (MOSI), U1.16 (PDI_/_MOSI_/_PCINT2_PB2)
MOSI-2560: J8.4 (MOSI), U13.21 (MOSI/PCINT2_PB2)
unnamed: C2.1, R5.1, U1.1 (XTAL1), Y1.1
unnamed: C3.1, R5.2, U1.2 (PC0_XTAL2), Y1.2
unnamed: C10.1, R9.2, U1.13 (/_HWB*_/_AIN6_/_T0_/_INT7_PD7)
unnamed: C9.1, C11.1, CR1.3 (INPUT), D1.2 (K), R20.1
unnamed: C20.1, R20.2, R21.1, U7.3 (1IN+)
unnamed: C24.1, U4.5 (CAP+)
unnamed: C24.2, U4.3 (CAP-)
unnamed: C26.2, F1.1, Q1.3 (D), U1.31 (UVCC)
unnamed: C38.1, R34.2, U12.1 (+IN)
unnamed: C46.1, C50.1, R42.2, R43.1, U14.3 (+IN)
unnamed: C52.1, R51.2, U11.6 (VIN2-)
unnamed: C52.2, U11.7 (VOUT2), U12.8 (-IN)
unnamed: C55.2, R48.1, U11.5 (VIN2+)
unnamed: C69.1, U13.98 (AREF)
unnamed: C75.1, R66.2
unnamed: C79.1, R70.2
unnamed: C81.1, R74.2
unnamed: D1.1 (A), J1.1
unnamed: D2.1 (K), U1.10 (INT5/_AIN3_PD4)
unnamed: D2.2 (A), R2.1
unnamed: D3.1 (K), U1.11 (XCK_AIN4_/_PCINT12_PD5)
unnamed: D3.2 (A), R3.1
unnamed: D4.2 (A), R14.1
unnamed: D5.2 (A), R16.1
unnamed: F1.2, J2.1
unnamed: J3.1 (In), U20.3 (S1)
unnamed: J3.2 (Ext), U20.14 (S2)
unnamed: J4.1 (In), U20.11 (S3)
unnamed: J4.2 (Ext), U20.6 (S4)
unnamed: J5.1 (In), U21.3 (S1)
unnamed: J5.2 (Ext), U21.14 (S2)
unnamed: J6.1 (In), U21.11 (S3)
unnamed: J6.2 (Ext), U21.6 (S4)
unnamed: JP3.1, R32.2
unnamed: JP3.2, U10.1 (VOUT1), U10.2 (VIN1-)
unnamed: JP4.1, R37.2
unnamed: JP5.1, R45.2
unnamed: JP5.2, U10.6 (VIN2-), U10.7 (VOUT2)
unnamed: Q1.1 (G), U7.1 (1OUT)
unnamed: R1.1, U5.9 (S8)
unnamed: R4.1, U5.10 (S7)
unnamed: R6.1, U5.11 (S6)
unnamed: R7.1, U5.12 (S5)
unnamed: R11.1, U5.7 (S4)
unnamed: R12.2, U1.8 (RXD1_/_AIN1_/_INT2_PD2)
unnamed: R13.1, U1.9 (TXD1_/_INT3_PD3)
unnamed: R14.2, U7.6 (2IN-), U7.7 (2OUT)
unnamed: R15.1, U5.6 (S3)
unnamed: R17.1, U5.5 (S2)
unnamed: R19.1, U5.4 (S1)
unnamed: R36.2, R48.2, U11.1 (VOUT1), U11.2 (VIN1-), U12.4 (REF)
unnamed: R41.1, U13.33 (XTAL2), Y2.1
unnamed: R41.2, U13.34 (XTAL1), Y2.3
unnamed: R44.1, U15.9 (S8)
unnamed: R46.1, U15.10 (S7)
unnamed: R47.2, U12.5 (FB), U12.6 (OUT)
unnamed: R50.1, U15.11 (S6)
unnamed: R52.1, U15.12 (S5)
unnamed: R53.1, U15.7 (S4)
unnamed: R54.1, U15.6 (S3)
unnamed: R55.1, U15.5 (S2)
unnamed: R56.1, U15.4 (S1)
unnamed: R57.2, U16.7
unnamed: R64.1, R66.1, U18.11 (S6)
unnamed: R65.1, U18.12 (S5)
unnamed: R67.1, U18.7 (S4)
unnamed: R68.1, R70.1, U18.10 (S7)
unnamed: R69.1, U18.6 (S3)
unnamed: R71.1, U18.5 (S2)
unnamed: R72.1, R74.1, U18.9 (S8)
unnamed: R73.1, U18.4 (S1)
PB7: U7.5 (2IN+), U13.26 (OC0A/OC1C/PCINT7_PB7)
PD-AD8130: R33.1, U12.3 (PD*), U13.87 (PK2_ADC10/PCINT18)
PE0: R13.2, U13.2 (RXD0/PCINT8_PE0)
PE1: R12.1, U13.3 (TXD0_PE1)
RD+: R30.2, U1.29 (D+)
RD-: R29.2, U1.30 (D-)
RESET: C10.2, C43.1, D7.1 (A), J8.5 (~RST), JP1.1 (A), JP1.2 (B), R40.2, S1.1, U13.30 (*RESET)
RESET-16u2: D6.1 (A), J7.5 (~RST), R35.2, U1.24 (RESET*PC1_/_dW)
RESIS_A0: R76.1, U13.58 (PC5_A13), U18.1 (A0)
RESIS_A1: R78.1, U13.57 (PC4_A12), U18.16 (A1)
RESIS_A2: R80.1, U13.56 (PC3_A11), U18.15 (A2)
RESIS_EN: R77.2, U13.60 (PC7_A15), U18.2 (EN)
RESIS_MUX: U17.3 (S1B), U17.6 (S2B), U18.8 (D)
RESIS_MUX_OUT: C75.2, C79.2, C81.2, R64.2, R65.2, R67.2, R68.2, R69.2, R71.2, R72.2, R73.2, U17.10 (S3B), U17.13 (S4B)
RFB: R1.2, R4.2, R6.2, R7.2, R11.2, R15.2, R17.2, R19.2, U6.4 (RFB)
RFB_MUX_IN: R57.1, U5.8 (D), U6.5 (VIN)
RG: R44.2, R46.2, R50.2, R52.2, R53.2, R54.2, R55.2, R56.2, U16.3 (Rg)
RG_A0: R58.1, U13.39 (OC5B_PL4), U15.1 (A0)
RG_A1: R60.1, U13.38 (OC5A_PL3), U15.16 (A1)
RG_A2: R62.1, U13.37 (T5_PL2), U15.15 (A2)
RG_EN: R59.2, U13.41 (PL6), U15.2 (EN)
RG_MUX: U15.8 (D), U16.2 (Rg)
SCL: R8.2, U6.16 (SCL), U13.43 (SCL/INT0_PD0)
SCLK-16u2: J7.3 (SCK), U1.15 (SCLK_/_PCINT1_PB1)
SCLK-2560: J8.3 (SCK), U13.20 (SCK/PCINT1_PB1)
SDA: R10.2, U6.15 (SDA), U13.44 (SDA/INT1_PD1)
SHEILD1: R36.1, R38.2, U20.15 (D2)
SHEILD2: R31.2, R32.1, U20.7 (D4)
SHEILD3: R37.1, R39.2, U21.15 (D2)
SHEILD4: R45.1, R49.2, U21.7 (D4)
SIGNAL: R47.1, U11.3 (VIN1+), U17.4 (D1)
UGND: C29.1, J2.5, JP2.1 (A), L1.1, R25.2, R26.2, U1.28 (UGND)
VCC-16u2: 16MHz1.4 (V+), C1.1, C4.1, C5.1, C6.1, C7.1, C8.1, C13.1, C15.1, C16.1, C18.1, C19.1, C21.1, C22.1, C23.1, C39.1, C40.1, C41.1, C42.1, C44.1, C45.1, C49.1, C51.1, C53.1, C54.1, C57.1, C58.1, C59.1, C61.1, C62.1, C64.1, C66.1, C67.1, C68.1, C70.1, C71.1, C72.1, C82.1, C83.1, CR1.2 (OUTPUT), D6.2 (K), D7.2 (K), J7.2 (VCC), J8.2 (VCC), Q1.2 (S), R2.2, R3.2, R8.1, R10.1, R16.2, R35.1, R40.1, R42.1, U1.4 (VCC), U1.32 (AVCC), U3.2 (VIN), U4.2 (V+), U5.13 (VDD), U6.9 (DVDD), U6.10 (AVDD1), U6.11 (AVDD2), U7.8 (VCC+), U8.1 (VIN), U8.3 (ON/*OFF), U9.7 (V+), U10.8 (VS+), U11.8 (VS+), U12.7 (+VS), U13.10 (VCC), U13.31 (VCC), U13.61 (VCC), U13.80 (VCC), U13.100 (AVCC), U14.7 (V+), U15.13 (VDD), U16.8 (Vs+), U17.16 (VDD), U18.13 (VDD), U20.13 (VDD), U20.16 (POSFV), U21.13 (VDD), U21.16 (POSFV)
VOUT: C38.2, U6.6 (VOUT)
VUCAP: C29.2, U1.27 (UCAP)
XTAL-EN: 16MHz1.1 (OE), R18.1, U13.35 (ICP4_PL0)
jackD+: J2.3, R25.1, R30.1
jackD-: J2.2, R26.1, R29.1

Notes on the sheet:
OE pin = "H" or "open" : Specified frequency output. OE pin = "L" : Output is high impedance.
Wide band frequency Fixed current source (Ar-Rawi et al 2009 and Harder et al 2016)
Bypass Capasitors
10uF ceramic capacitor 1206
ELECTRODE1 SHEILD DRIVE AND VREF BUFFER
Ultraprecision, Low Noise, 2.048 V XFET Voltage Reference
Ultraprecision, Low Noise, 5.00 V XFET Voltage Reference
-5.0 V Voltage Source (25mA)
Sheilded Drives (Jiang et al 2018)
IN-AMP-REF BUFFER
Instrumentation Amplifier (IN-AMP AD8421 SOIC)
On-The-Fly-Calibration Multiplexer/Switch (as in Analog Devices application note CN-0217)
RFB Gain Adjustment Multiplexer/Switch (as in Analog Devices application note CN-0217)
IN-AMP GAIN Multiplexer/Switch
ELECTRODES
ELECTRODE3 DRIVE (2V048) AND ELECTRODE3 SHEILD (2V048)
ELECTRODE4 SHEILD DRIVE
ELECTRODE2 SHEILD DRIVE
- 19 digital inputs and outputs
pin 22 pin 23 pin 24 pin 25 pin 26
pin 30 pin 31 pin 32 pin 33 pin 34
pin 47 pin 46 pin 45 pin 44 pin 43
pin 21 pin 20
pin A8 pin A9 pin A10
pin 49
CG0603MLC-05E ESD Suppressors / TVS Diodes Chip Guard 0603 5 Volts
MF-MSMF050-2 FUSE Polymeric PTC Resettable Fuse 15V 500mA Ih Surface Mount 1812 (4532 Metric), Concave
POWER LED
MCU PROGRAMMER
MCU ATMEGA2560
P$1 P$2 = connections to the metal shell of the USB connector and wire to ground.
pin 13
Andrew L. Allison

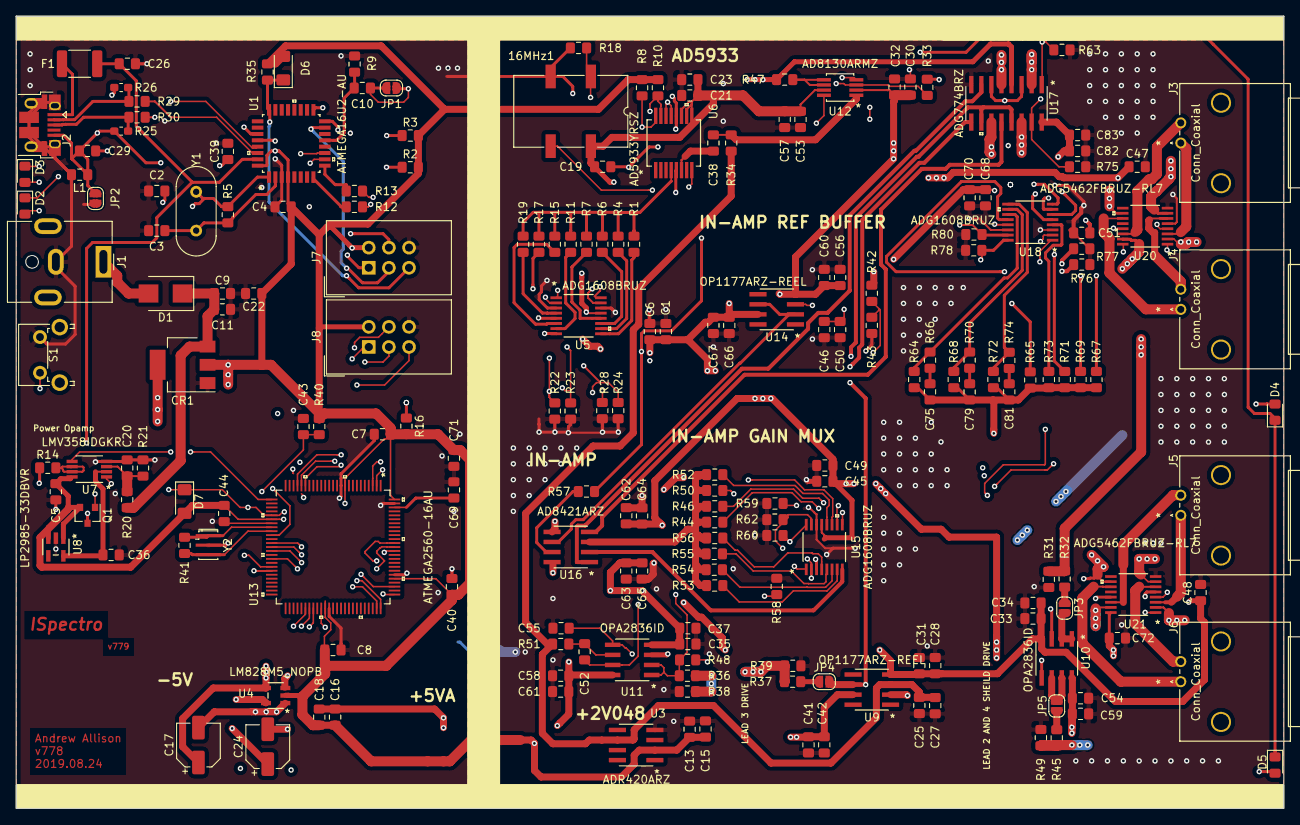
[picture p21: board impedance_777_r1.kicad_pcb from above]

Board: 4 copper layers, 160.0 x 100.0 mm, 200 parts (1 on the bottom side), 133 nets.

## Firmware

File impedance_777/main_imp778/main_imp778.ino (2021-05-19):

#include "Wire.h"
#include <stdio.h>
#include <string.h>
#include <limits.h>
#include <math.h>


#define button 2
#define SLAVE_ADDR 0x0D
#define ADDR_PTR 0xB0
#define START_FREQ_R1 0x82
#define START_FREQ_R2 0x83
#define START_FREQ_R3 0x84
#define FREG_INCRE_R1 0x85
#define FREG_INCRE_R2 0x86
#define FREG_INCRE_R3 0x87
#define NUM_INCRE_R1 0x88
#define NUM_INCRE_R2 0x89
#define NUM_SCYCLES_R1 0x8A
#define NUM_SCYCLES_R2 0x8B
#define RE_DATA_R1 0x94
#define RE_DATA_R2 0x95
#define IMG_DATA_R1 0x96
#define IMG_DATA_R2 0x97
#define TEMP_R1 0x92
#define TEMP_R2 0x93
#define CTRL_REG 0x80
#define CTRL_REG2 0x81
#define STATUS_REG 0x8F


// const float MCLK = 16.776*pow(10,6);// AD5933 Internal Clock Speed 16.776 MHz

const float MCLK = 16.000*pow(10,6);// AD5933 External Precision Clock Speed 16.000 MHz
const float start_freq = 1*pow(10,3);// Set start freq, < 100Khz
const float incre_freq = 1*pow(10,3);// Set freq increment
const int incre_num = 99;// Set number of increments,< 511
char state;


//////////////////////////////////////////////////////////////////////////////////////////////////////////////////////////////////////////////
//////////////////////////////////////////////////////////////////////////////////////////////////////////////////////////////////////////////
//  MAIN METHODS
//////////////////////////////////////////////////////////////////////////////////////////////////////////////////////////////////////////////
//////////////////////////////////////////////////////////////////////////////////////////////////////////////////////////////////////////////


void setup() {
  Wire.begin();
  Serial.begin(38400);

  // LED
  pinMode(LED_BUILTIN, OUTPUT); // REAR DATA TRANSFER LED
  pinMode(13, OUTPUT); // FRONT ORANGE INDICATOR LED

  // SG-615
  pinMode(49, OUTPUT); // XTAL-EN ENABLES AD5933 EXTERNAL XTAL
  
  // AD8130
  pinMode(A10, OUTPUT); // PD-AD8130 ENABLE CURRENT SOURCE

  // ADG774
  pinMode(A8, OUTPUT); // CAL_EN ADG774 CALIBRATION OR LEAD SELECTION 
  pinMode(A9, OUTPUT); // CAL_IN ADG774 CALIBRATION OR LEAD SELECTION 

  // ADG1608-1
  pinMode(30, OUTPUT); // RESIS_EN ADG1608 R/RC CALIBRATION SELECTION 
  pinMode(32, OUTPUT); // RESIS_A0 ADG1608 R/RC CALIBRATION SELECTION
  pinMode(33, OUTPUT); // RESIS_A1 ADG1608 R/RC CALIBRATION SELECTION
  pinMode(34, OUTPUT); // RESIS_A2 ADG1608 R/RC CALIBRATION SELECTION

  // ADG1608-2
  pinMode(43, OUTPUT); // RG_EN ADG1608 IN-AMP RESISTOR GAIN SELECTION
  pinMode(45, OUTPUT); // RG_A0 ADG1608 IN-AMP RESISTOR GAIN SELECTION
  pinMode(46, OUTPUT); // RG_A1 ADG1608 IN-AMP RESISTOR GAIN SELECTION
  pinMode(47, OUTPUT); // RG_A2 ADG1608 IN-AMP RESISTOR GAIN SELECTION

  // ADG1608-3
  pinMode(22, OUTPUT); // IN_AMP_EN ADG1608 RFB SELECTION
  pinMode(24, OUTPUT); // IN_AMP_A0 ADG1608 RFB SELECTION
  pinMode(25, OUTPUT); // IN_AMP_A1 ADG1608 RFB SELECTION
  pinMode(26, OUTPUT); // IN_AMP_A2 ADG1608 RFB SELECTION

  writeData(CTRL_REG,0x0);   //nop - clear ctrl-reg
  writeData(CTRL_REG2,0x10);   //reset ctrl register
  
  // SG-615
  digitalWrite(49, HIGH); // XTAL-EN ENABLES AD5933 EXTERNAL XTAL
  
  programReg();

  // Front LED three flashes to indicate setup
  flashLED();
}


void loop(){
  //Read state and enter FSM
    if(Serial.available()>0) {
      state = Serial.read();
      //FSM
      switch(state) {
        case 'A':  //Program Registers
          programReg();
          break;

        case 'B':  //Measure Temperature
          measureTemperature();
          break;

        case 'C':
          runSweep();
          delay(1000);
          break;

        case 'D':
          runCal1(); // R73 (1001 1k resistor)
          delay(1000);
          break;

        case 'E':
          runCal2(); // R71 (1002 10k resistor)
          delay(1000);
          break;

        case 'F':
          runCal3(); // R69 (101 100RO resistor)
          delay(1000);
          break;

        case 'G':
          runCal4(); // R67 (751 10k resistor)
          delay(1000);
          break;

        case 'H':
          runCal5(); // R65 (C65 actually 10nF cap)
          delay(1000);
          break;

        case 'I':
          runCal6();
          delay(1000);
          break;

        case 'J':
          runCal7();
          delay(1000);
          break;

        case 'K':
          runCal8();
          delay(1000);
          break;

        case 'L':
          onLED();
          delay(1000);
          break;

        case 'M':
          on774();
          break;
          
        case 'N':
          off774();
          break;
          
      /////Programming Device Registers/////
      }
      Serial.flush();
    }
}


//////////////////////////////////////////////////////////////////////////////////////////////////////////////////////////////////////////////
//////////////////////////////////////////////////////////////////////////////////////////////////////////////////////////////////////////////
//  SWEEP METHODS
//////////////////////////////////////////////////////////////////////////////////////////////////////////////////////////////////////////////
//////////////////////////////////////////////////////////////////////////////////////////////////////////////////////////////////////////////


void programReg(){
  // Set Range 1, PGA gain 1
  writeData(CTRL_REG,0x01); // # D8/0x80/10000000 0x01/1 // turn to 0x07 to change p-p to 1
  writeData(CTRL_REG2,0x08); // Enable AD5933 external clock setting (delete to turn off)
  // Set settling cycles
  writeData(NUM_SCYCLES_R1, 0x07);
  writeData(NUM_SCYCLES_R2, 0xFF);
  // Start frequency of 1kHz
  writeData(START_FREQ_R1, getFrequency(start_freq,1));
  writeData(START_FREQ_R2, getFrequency(start_freq,2));
  writeData(START_FREQ_R3, getFrequency(start_freq,3));
  // Increment by 1 kHz
  writeData(FREG_INCRE_R1, getFrequency(incre_freq,1)),
  writeData(FREG_INCRE_R2, getFrequency(incre_freq,2)),
  writeData(FREG_INCRE_R3, getFrequency(incre_freq,3));
  // Points in frequency sweep (100), max 511
  writeData(NUM_INCRE_R1, (incre_num & 0x001F00)>>0x08 );
  writeData(NUM_INCRE_R2, (incre_num & 0x0000FF));
}


//////////////////////////////////////////////////////////////////////////////////////////////////////////////////////////////////////////////
//////////////////////////////////////////////////////////////////////////////////////////////////////////////////////////////////////////////
//  RUN SWEEP
//////////////////////////////////////////////////////////////////////////////////////////////////////////////////////////////////////////////
//////////////////////////////////////////////////////////////////////////////////////////////////////////////////////////////////////////////


void runSweep() {
  short re;
  short img;
  double freq;
  double kfreq;
  double mag;
  double phase;
  double phasei;
  double phasex;
  double phasey;
  double gain;
  double impedance;
  double sys_phase;
  int i=0;
  int gf=1;
  double x;
  double y;
  double z;
  double t;
  programReg();

  
  LED(true);
  AD8130(true);
  ADG774('A');
  ADG1608_RC(0);
  ADG1608_GAIN(1);
  ADG1608_RFB(1);

  delay(500);
  
  writeData(CTRL_REG,(readData(CTRL_REG) & 0x07) | 0xB0); // 1. Standby '10110000' Mask D8-10 of avoid tampering with gains
  writeData(CTRL_REG,(readData(CTRL_REG) & 0x07) | 0x10); // 2. Initialize sweep
  writeData(CTRL_REG,(readData(CTRL_REG) & 0x07) | 0x20); // 3. Start sweep

  while((readData(STATUS_REG) & 0x07) < 4 ) {  // Check that status reg != 4, sweep not complete
    delay(1000); // delay between measurements
    int flag = readData(STATUS_REG)& 2;
    if (flag==2) {


      byte R1 = readData(RE_DATA_R1);
      byte R2 = readData(RE_DATA_R2);
      re = (R1 << 8) | R2;
      R1  = readData(IMG_DATA_R1);
      R2  = readData(IMG_DATA_R2);
      img = (R1 << 8) | R2;

      
      freq = start_freq + i*incre_freq;
      freq = freq/1000;
      
      // Serial.println(freq)
      double x = freq * 1.0;
      double y = (double)re * 1.0;
      double z = (double)img * 1.0;
      double t = measureTemperatureDouble();
      t = (double)t * 1.0;
      sendToPC(&x, &y, &z, &t);

      if((readData(STATUS_REG) & 0x07) < 4 ){ //Increment frequency
        writeData(CTRL_REG,(readData(CTRL_REG) & 0x07) | 0x30);
        i++;
        gf++;
      }
      //digitalWrite(LED_BUILTIN, LOW);    // turn the LED off by making the voltage LOW
    }
  }
//  writeData(CTRL_REG,0xA0);
  writeData(CTRL_REG,(readData(CTRL_REG) & 0x07) | 0xA0); //Power down

  delay(2000);
  allLOW();
  
}


//////////////////////////////////////////////////////////////////////////////////////////////////////////////////////////////////////////////
//////////////////////////////////////////////////////////////////////////////////////////////////////////////////////////////////////////////
//  RUN CAL 1
//////////////////////////////////////////////////////////////////////////////////////////////////////////////////////////////////////////////
//////////////////////////////////////////////////////////////////////////////////////////////////////////////////////////////////////////////


void runCal1() {
  short re;
  short img;
  double freq;
  double kfreq;
  double mag;
  double phase;
  double phasei;
  double phasex;
  double phasey;
  double gain;
  double impedance;
  double sys_phase;
  int i=0;
  int gf=1;
  double x;
  double y;
  double z;
  double t;
  programReg();

  // LED
  digitalWrite(LED_BUILTIN, HIGH); // REAR DATA TRANSFER LED
  digitalWrite(13, HIGH); // FRONT ORANGE INDICATOR LED

  // AD8130
  digitalWrite(A10, HIGH); // PD-AD8130 ENABLE CURRENT SOURCE

  // ADG774
  digitalWrite(A8, LOW); // CAL_EN ADG774 CALIBRATION OR LEAD SELECTION 
  digitalWrite(A9, HIGH); // CAL_IN ADG774 CALIBRATION OR LEAD SELECTION 

  // ADG1608-1
  digitalWrite(30, HIGH); // RESIS_EN ADG1608 R/RC CALIBRATION SELECTION 
  digitalWrite(32, LOW); // RESIS_A0 ADG1608 R/RC CALIBRATION SELECTION
  digitalWrite(33, LOW); // RESIS_A1 ADG1608 R/RC CALIBRATION SELECTION
  digitalWrite(34, LOW); // RESIS_A2 ADG1608 R/RC CALIBRATION SELECTION

  // ADG1608-2
  digitalWrite(43, HIGH); // RG_EN ADG1608 IN-AMP RESISTOR GAIN SELECTION
  digitalWrite(45, LOW); // RG_A0 ADG1608 IN-AMP RESISTOR GAIN SELECTION
  digitalWrite(46, LOW); // RG_A1 ADG1608 IN-AMP RESISTOR GAIN SELECTION
  digitalWrite(47, LOW); // RG_A2 ADG1608 IN-AMP RESISTOR GAIN SELECTION

  // ADG1608-3
  digitalWrite(22, HIGH); // IN_AMP_EN ADG1608 RFB SELECTION
  digitalWrite(24, LOW); // IN_AMP_A0 ADG1608 RFB SELECTION
  digitalWrite(25, LOW); // IN_AMP_A1 ADG1608 RFB SELECTION
  digitalWrite(26, LOW); // IN_AMP_A2 ADG1608 RFB SELECTION

  writeData(CTRL_REG,(readData(CTRL_REG) & 0x07) | 0xB0); // 1. Standby '10110000' Mask D8-10 of avoid tampering with gains
  writeData(CTRL_REG,(readData(CTRL_REG) & 0x07) | 0x10); // 2. Initialize sweep
  writeData(CTRL_REG,(readData(CTRL_REG) & 0x07) | 0x20); // 3. Start sweep

  while((readData(STATUS_REG) & 0x07) < 4 ) {  // Check that status reg != 4, sweep not complete
    delay(1000); // delay between measurements

    int flag = readData(STATUS_REG)& 2;
    if (flag==2) {
      //digitalWrite(LED_BUILTIN, HIGH);   // turn the LED on (HIGH is the voltage level)


      byte R1 = readData(RE_DATA_R1);
      byte R2 = readData(RE_DATA_R2);
      re = (R1 << 8) | R2;
      R1  = readData(IMG_DATA_R1);
      R2  = readData(IMG_DATA_R2);
      img = (R1 << 8) | R2;
      freq = start_freq + i*incre_freq;
      freq = freq/1000;
      // Serial.println(freq)
      double x = freq * 1.0;
      double y = (double)re * 1.0;
      double z = (double)img * 1.0;
      double t = measureTemperatureDouble();
      t = (double)t * 1.0;
      sendToPC(&x, &y, &z, &t);

      if((readData(STATUS_REG) & 0x07) < 4 ){ //Increment frequency
        writeData(CTRL_REG,(readData(CTRL_REG) & 0x07) | 0x30);
        i++;
        gf++;
      }
      //digitalWrite(LED_BUILTIN, LOW);    // turn the LED off by making the voltage LOW
    }
  }
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

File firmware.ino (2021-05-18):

#include "Wire.h" // library for I2C communication to AD5933
#include <stdio.h>

// AD5933 REGISTER MAP
#define Control_D15_to_D8 0x80                            // Read/write
#define Control_D7_to_D0 0x81                             // Read/write
#define Start_frequency_D23_to_D16 0x82                   // Read/write
#define Start_frequency_D15_to_D8 0x83                    // Read/write
#define Start_frequency_D7_to_D0 0x84                     // Read/write
#define Frequency_increment_D23_to_D16 0x85               // Read/write
#define Frequency_increment_D15_to_D8 0x86                // Read/write
#define Frequency_increment_D7_to_D0 0x87                 // Read/write
#define Number_of_increments_D15_to_D8 0x88               // Read/write
#define Number_of_increments_D7_to_D0 0x89                // Read/write
#define Number_of_settling_time_cycles_D15_to_D8 0x8A     // Read/write
#define Number_of_settling_time_cycles_D7_to_D0 0x8B      // Read/write
#define Status_D7_to_D0 0x8F                              // Read only
#define Temperature_data_D15_to_D8 0x92                   // Read only
#define Temperature_data_D7_to_D0 0x93                    // Read only
#define Real_data_D15_to_D8 0x94                          // Read only
#define Real_data_D7_to_D0 0x95                           // Read only
#define Imaginary_data_D15_to_D8 0x96                     // Read only
#define Imaginary_data_D7_to_D0 0x97                      // Read only

#define Slave_Address 0x0D
#define Address_Pointer 0xB0

// Global Variables
const char prefixDelimiter = '<';
const char suffixDelimiter = '>';

boolean readingBuffer = false;
boolean newInput = false;

const byte bufferSize = 40;
char inputBuffer[bufferSize];
byte bytesReceived = 0;
int PGA_BIN = 0b1;

char charactersFromPC[bufferSize] = {0};
int passedInt = 0;
float passedFloat = 0.0;

int globalFlashDelayMs = 1000;
boolean stateVar = true;
byte incomingByte;

short re;
short img;

double kfreq;
double mag;
double phase;
double phasei;
double phasex;
double phasey;
double gain;
double impedance;
double sys_phase;

int scanNumberAtFrequency = 1;
int i=0;
int gf=1;

double sweepUnderWay = 0.0;

double x;
double y;

double xcal;
double ycal;
double xccal;
double yccal;

double t;

const float external_clock = 16000000.0; // 16 Mhz external clock frequency
float Start_Frequency = 1000.0; // 1kHz starting frequency
float Increment_Frequency = 1000.0; // 1kHz step size
int Number_of_Increments = 99; // 99 steps
int Sweep_delay = 333;

boolean AD8130_STATE = true;


int ADG1608_RC_STATE = 0;
int ADG1608_RC_STATE2 = 2;
int ADG1608_RC_STATE3 = 3;

char ADG774_STATE = 'A';
char ADG774_STATE2 = 'A';
char ADG774_STATE3 = 'A';

int ADG1608_GAIN_STATE = 1;
int ADG1608_RFB_STATE = 1;


int PGA_STATE = 1;
int VOLTAGE_STATE = 1;
int VOLTAGE_BIN = 0;
int read_data = 0b0;

int flash_delay = 1000;

double f = Start_Frequency;
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

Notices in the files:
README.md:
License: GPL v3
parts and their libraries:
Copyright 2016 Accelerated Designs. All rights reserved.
